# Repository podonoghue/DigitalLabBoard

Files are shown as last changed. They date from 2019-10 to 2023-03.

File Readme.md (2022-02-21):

# DigitalLabBoard
Digital Board for Undergraduate Laboratory  
Includes CPLD Programmer for XC2C64A

Folders:
* __Code_Design__ Software applications and firmware for on board microcontroller 
* __CommandLine__ Command line files using Xilinx S/W to prepare test images 
* __Documents__ Various resources associated with the project 
* __PCB_Design__ Altium Designer files for PCB 
* __Release_Files__ Release files for installation
* __VHDL_TestHardware__ Simple test projects for the CPLD 
 
[Lab manual](https://raw.githubusercontent.com/podonoghue/DigitalLabBoard/master/Laboratory%20Manual.pdf)
 
[Digital lab board documentation](https://raw.githubusercontent.com/podonoghue/DigitalLabBoard/master/PCB_Design/DigitalLabBoard/DigitalLabBoard_V4.PDF)  

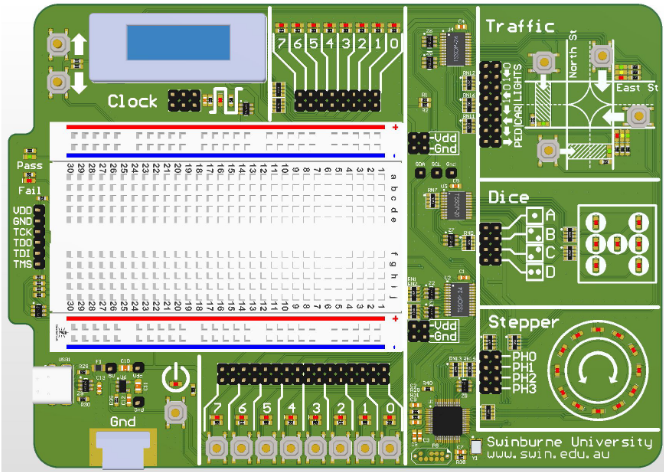
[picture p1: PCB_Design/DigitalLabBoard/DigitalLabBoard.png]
An image Board Image


[CPLD programmer documentation](https://raw.githubusercontent.com/podonoghue/DigitalLabBoard/master/PCB_Design/CPLD_Programmer/CPLD_Programmer_V2.PDF)  Note that a version of the programmer is built into the above lab board.

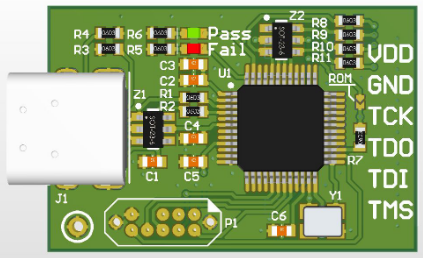
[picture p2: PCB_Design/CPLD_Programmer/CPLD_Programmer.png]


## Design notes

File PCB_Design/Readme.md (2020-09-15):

# PCB Designs

Folders:
* __CPLD_Programmer__ PCB design for standalone programmer
* __DigitalLabBoard__ PCB design for digitallab board

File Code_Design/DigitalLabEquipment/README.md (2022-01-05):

# Code for DigitalLabBoard
This code provides the following functions for the board:  
- Button debouncing and output for Button module.  
- Button debouncing, input monitoring and outputs for Traffic module.  
- Input monitoring and output LED control for the stepper module.  
- Control of the on-board clock generator.  
- SVD JTAG programmer.

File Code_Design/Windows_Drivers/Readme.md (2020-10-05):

# DigitalLabBoard - Driver
Windows Driver for Digital Lab Board and standalone CPLD programmer

Due to the need to create and sign windows driver .CAT files this sofwtare cannot be built on Linux.

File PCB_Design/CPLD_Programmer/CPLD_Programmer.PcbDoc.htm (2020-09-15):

Reporting Options

# File in Previous Format

Date | : | 15/09/2020
Time | : | 4:25:42 PM
Filename | : | \\vmware-host\Shared Folders\Documents\Development\DigitalLabBoard\PCB_Design\CPLD_Programmer\CPLD_Programmer.PcbDoc

Version | Warning

This file was generated by an earlier version of the software

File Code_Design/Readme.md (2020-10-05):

# DigitalLabBoard - Software
Software for Digital Lab Board and standalone CPLD programmer

Projects:
* __Bootloader_DigitalLogicBoard__ Software for boot-loader
* __Convert_XSVF_C__ Converts XSVF files to C array for embedding
* __CPLD_ProgrammerApp__ Windows application for CPLD programmer
* __DigitalLabEquipment__ Software for board
* __Documentation__ Links to Readme files
* __GenerateTables__ Creates tables describing JTAG state-machine and permitted transitions.
* __KinetisBootloaderApp__ WIN32 boot-loader application
* __Linux_Installer__ Linux installer (DEB file)
* __PackageFiles__ Where files are collected
* __PARSE_JEDEC__ 
* __Parse_XSVF_To_C__  
* __Shared__ Some files that get bundled when installer is built
* __Windows_Drivers__ WINUSB drivers for Windows (none needed for Linux)
* __Windows_Installer__ Windows installer (MSI file)
* __compareFiles__ 
* __xsvf_player__ Software for CPLD programmer
* __xsvf_rom_player__ Software for stand-alone CPLD programmer i.e. embedded CPLD XSVF array

This is an  __Eclipse__  workspace.  
Some projects required the __USBDM plugin__.

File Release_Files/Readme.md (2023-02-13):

# DigitalLabBoard
Release files for Digital Board for Undergraduate Laboratory  

* __Digital_Lab_Board_Drivers_1_1_0_Win_x64__ Signed drivers for Windows
* __DigitalLabEquipment_2023_02_14.elf__      Flash image for use with custom Kinetis bootloader
* __eee20001-lab-software_2.2.0.0-1-x86_64.deb__ CPLD programming software for Linux
* __EEE20001-Lab-Software-2020-01.msi__          CPLD programming software for Windows (original release)
* __EEE20001-Lab-Software-2023-02.msi__          CPLD programming software for Windows (latest)

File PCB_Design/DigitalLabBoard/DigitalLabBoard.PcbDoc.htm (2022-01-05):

Reporting Options

# File in Previous Format

Date | : | 22-Oct-21
Time | : | 3:15:27 PM
Filename | : | Z:\Documents\Development\DigitalLabBoard\PCB_Design\DigitalLabBoard\DigitalLabBoard.PcbDoc

Version | Warning
6.3 | CAUTION - Via connections to both hatched and solid signal layer polygons are now controlled by the polygon connect style rule. Re-pouring polygons may result in physical copper differences.
Summer 09 | CAUTION - File contains old violation objects. These violations are no longer supported & will not be loaded. Please run DRC after opening this file in order to refresh the violations.
Summer 09 | CAUTION - Existing testpoint rules and settings are used as fabrication testpoint information.
Release 12 | CAUTION - Air Gap Width previously controlled by Clearance rule is now controlled by Polygon Connect Style rule's newly introduced Air Gap Width (set to default value). Suggest reviewing each Polygon Connect Style rule's Air Gap Width attribute for correctness.
Release 13 | CAUTION - Silkscreen Over Component Pads Rules are converted to Silk To Solder Mask Clearance Rules. Suggest examining rule scopes for accuracy.

This file was generated by an earlier version of the software

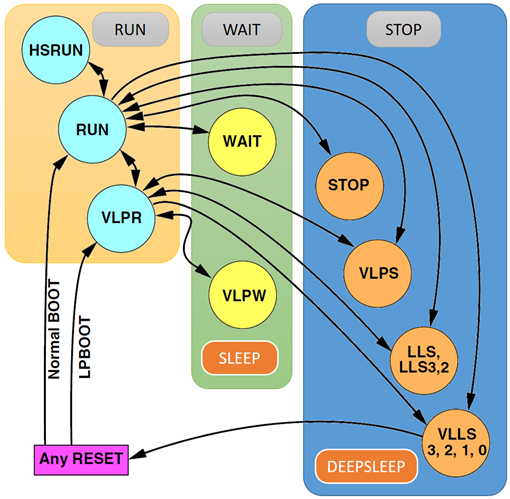
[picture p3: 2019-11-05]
Code_Design/KinetisBootloader/Project_Headers/KinetisPowerModes.png

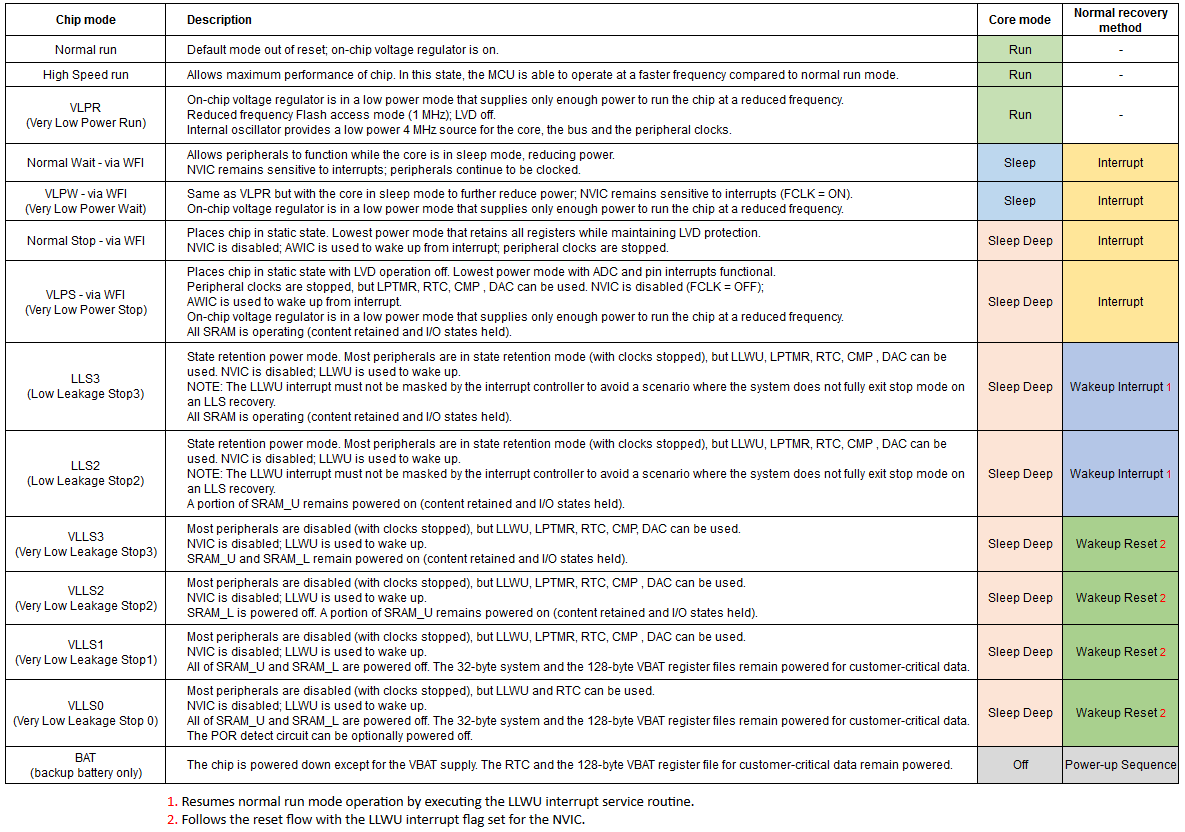
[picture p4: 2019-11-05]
Code_Design/KinetisBootloader/Project_Headers/PowerModes.png

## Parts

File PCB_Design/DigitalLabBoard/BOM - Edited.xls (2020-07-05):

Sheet: BOM Report
Bill of Materials |  |  | Bill of Materials for Project [DigitalLabBoard.PrjPCB] (No PCB Document Selected)
Source Data From: |  | DigitalLabBoard.PrjPCB
Project: |  | DigitalLabBoard.PrjPCB
Variant: |  | None
Logic Board |  |  |  |  |  |  | Unit cost |  | Per Board cost
Footprint | Comment | Farnell PN | Digikey | Designator | Description | Quantity | Small Qty | Large Qty | Small Qty | Large Qty
 |  |  |  |  | LCSC PCBA | 1 | $22.00 | $9.00 | $22.00 | $9.00
TSQFP50P900X900-48M | MK20DX128VLF5 | 2133571 (86 only) | MK20DX128VLF50-ND | U1 | 50MHz Cortex-M4 MCU | 1 | $8.86 | $7.01 | $8.86 | $7.01
USB4085-GF-A | USB4085-GF-A | 2924867 | 2073-USB4085-GF-ACT-ND | J8 | USB - C USB 2.0 Receptacle | 1 | $2.05 | $1.60 | $2.05 | $1.60 |  |  |  |  | $625.00
HDR1X6 straight | Header 1X6 | 1835481 | 609-3272-ND | P9 | Amphenol ICC 68000-106HLF | 1 | $0.55 | $0.98 | $0.55 | $0.98
HDR2X2S | Header 2x2 | 1622403 | 609-5699-ND/ A26534-02-ND | P10, P11 | Amphenol 77313-118-04LF/ TE Connectivity 4-102977-0-02 (longer pins) | 2 | $0.82 | $0.54 | $1.64 | $1.08 |  |  |  |  | $360.00
HDR2X3S | Header 2x3 | 2886106 | 609-5700-ND | P7 | Amphenol 77313-118-06LF | 1 | $0.58 | $0.38 | $0.58 | $0.38 |  |  | 100 | $58.37 | $5837.00
HDR2X4S | Header 2x4 |  | 609-5701-ND | P5, P6 | Amphenol 77313-118-08LF | 2 | $0.81 | $0.58 | $1.62 | $1.16 |  |  |  |  | $6822.00
HDR2X8S | Header 2x8 |  | 609-5704-ND | P1, P2, P3, P4 | Amphenol 77313-118-16LF | 4 | $1.11 | $0.83 | $4.44 | $3.32
Bumper_RBS-2 | Plastic Bumper | 1800864 1800862 | backup - RPC4821-ND | M1, M2, M3, M4, M5, M6, M7 | Plastic bumper/foot | 7 | $0.09 | $0.08 | $0.66 | $0.55 |  | Other | 100 | 32 | $3200.00
 |  |  |  |  |  |  |  | Parts | $20.40 | $16.08
 |  |  |  |  |  |  |  | 125 | $14.34 |  |  |  |  |  | $10022.00
 |  |  |  |  |  |  |  | 250 | $13.68
Breadboard - 300 holes | Breadboard - 300 Hole |  |  | B1 | Breadboard - 300 holes | 1 | $5.00 | $5.00 | $5.00 | $5.00 |  |  |  |  |  | Digikey online Quote
OLED_Display_128x32 | OLED_Display |  |  | OLED | OLED Display 128x32 pixels, I2C interface | 1 | $2.00 | $2.00 | $2.00 | $2.00 |  |  | Units | Cost | Total | 125 | 250
USB Type-A to USB-C R/A | USB Lead |  |  |  | USB Type-A to USB-C R/A lead | 1 | $6.00 | $6.00 | $6.00 | $6.00 | Base Board | Assembly | 250 | $9.00 | $2250.00
Decor 002560 | 900ml Plastic Box |  |  |  | Tellfresh Storer, Oblong 900ml, 203x143x53 | 1 | $3.33 | $3.33 | $3.33 | $3.33 |  | Parts | 125 | $14.34 | $1792.50 | $1792.5 | $3420
Patch Leads | 6" leads |  |  |  | M-M individual 6" leads - set of 10 | 1 | $3.38 | $2.50 | $3.38 | $2.50 |  | Other | 125 | $24.10 | $3012.92
Patch Leads | 6" leads |  |  |  | M-F individual 6" leads - set of 15 | 1 | $5.05 | $3.75 | $5.05 | $3.75 |  |  |  |  | $7055.42
Programming Lead | 3" lead |  |  |  | 6-way F-F 3" lead - 1 only | 1 | $2.06 | $1.52 | $2.06 | $1.52
 |  | Digikey cart | https://www.digikey.com.au/BOM/View?id=8130251 |  |  |  | $10.48 | Other | $26.82 | $24.10 | CPLD | Assembly | 250 | $1.22 | $305.00
CPLD Breakout |  |  |  |  |  |  |  |  |  |  |  | Parts | 125 | $8.35 | $1043.75 | $1043.75 | $1980
Footprint | Comment | Farnell PN | Digikey | Designator | Description | Quantity |  |  |  |  |  |  |  |  | $1348.75
CPLD Breakout | LCSC PCBA |  |  |  | LCSC PCBA | 1 |  | $1.22 | $0.00 | $1.22
 |  |  |  |  |  |  |  |  |  |  | Power | Assembly | 250 | $1.22 | $305.00
XC2C64A-7VQG44C | Xilinx CPLD | 2831286 | Backup 122-1410-ND |  |  | 1 | $5.28 | $5.27 | $5.28 | $5.27 |  | Parts | 125 | $2.29 | $286.25 | $286.25 | $520
HDR1x20 straight | Header 1x20 | 2892385 | 609-3253-ND |  | Amphenol ICC 68000-120HLF | 2 | $1.53 | $1.16 | $3.06 | $2.32 |  |  |  |  | $591.25
HDR1X6 straight | Header 1X6 | 1835481 | 609-3272-ND |  | Amphenol ICC 68000-106HLF | 1 | $0.55 | $0.98 | $0.55 | $0.98
 |  | Digikey cart | https://www.digikey.com.au/BOM/View?id=8130245 |  |  |  |  | Parts | $8.89 | $8.57 |  |  |  |  | $8995.42
 |  |  |  |  |  |  |  | 125 | $8.35
 |  |  |  |  |  |  |  | 250 | $7.92
 |  |  |  |  |  |  |  |  |  |  | Phase 2 | $7000.00 | extra 125
Breadboard Power
Footprint | Comment | Farnell PN | Digikey | Designator | Description | Quantity |  |  |  |  | 125 | $90.00 | $11250.00
Breadboard-power | LCSC PCBA |  |  |  | LCSC PCBA | 1 |  | $1.22 | $0.00 | $1.22 | 125 | $25.00 | $3125.00
 |  |  |  |  |  |  |  |  |  |  |  |  | $14375.00
HDR2X2S | Header 2x2 | 1622403 | 609-5699-ND | P1, P2 | Amphenol 77313-118-04LF | 2 | $0.40 | $0.26 | $0.80 | $0.52
HDR1X2S | Header, 2-Pin | 2751379 | 609-3500-ND | P3, P4 | Amphenol 68000-102HLF | 2 | $0.30 | $0.20 | $0.60 | $0.40
BCS-102-L-D-TE | Header 2x2, Female | 2984530 | SAM1008-02-ND | P5, P6 | Samtec BCS-102-L-D-TE | 2 | $1.05 | $0.75 | $2.10 | $1.50
 |  | Digikey cart | https://www.digikey.com.au/BOM/View?id=8130238 |  |  |  |  | Parts | $3.50 | $2.42 | 50 | 200
 |  |  |  |  |  |  |  | 125 | $2.29
 |  |  |  | Sparkfun PRT-10366 | Jumper Wire - 0.1", 6-pin, 4" |  |  | 250 | $2.08
 |  |  |  | Robot Gear SKU-002545 | Jumper Wire - 0.1", 6-pin, 4"
 |  |  |  | Pololu DIY | https://www.pololu.com/category/71/wires-with-pre-crimped-terminals
 |  |  |  |  |  |  |  |  |  |  | 635.67 | 2356.19

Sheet: Leads
 |  |  | /set | /set
 |  |  |  |  |  |  |  | 125
https://www.pololu.com/product/3330 | Wires with Pre-Crimped Terminals 10-Pack F-F 3" Black | $2.12 | 0.1 | $0.21 | 1 | 1 + 1 + 1 + 2 Makes 10 sets of programming cables | $2.12 | 12.5 | $26.50
https://www.pololu.com/product/3332 | Wires with Pre-Crimped Terminals 10-Pack F-F 3" Red | $2.12 | 0.1 | $0.21 | 1 |  | $2.12 | 12.5 | $26.50
https://www.pololu.com/product/1806 | Wires with Pre-Crimped Terminals 50-Piece 10-Color Assortment F-F 3" | $7.99 | 0.1 | $0.80 | 1 |  | $7.99 | 12.5 | $99.88
https://www.pololu.com/product/1905 | 0.1" (2.54mm) Crimp Connector Housing: 1x6-Pin 10-Pack | $0.71 | 0.2 | $0.14 | 2 |  | $1.42 | 25 | $17.75
 |  |  |  | $1.36
https://www.pololu.com/product/1702 | Premium Jumper Wire 50-Piece 10-Color Assortment M-M 6" | $11.24 | 0.2 | $2.25 | 2 | 2 + 3 Makes 10 sets of jump leads | $22.48 | 25 | $281.00
https://www.pololu.com/product/1701 | Premium Jumper Wire 50-Piece 10-Color Assortment M-F 6" | $11.24 | 0.3 | $3.37 | 3 |  | $33.72 | 37.5 | $421.50
 |  |  |  | $6.99 |  |  | $6.98 |  | $873.12
 |  | M-M | M-F | CPL M-M | PWR M-M
E1 | P1 | 2 | 6 |  | 2
 | P2 | 2 | 4
 | P3 |  | 5 | 2
 | P4 | 8 | 3 | 2
E2 | P1-3 |  | 8 | 2
 | P4 | 2 | 2
E3 | P1 |  | 6 | 2
 | P2a |  | 5 | 2
 | P2b |  | 5 | 2
 | P2c |  | 6 | 2
 | P3 | 5 | 3 |  | 2
 | P4 |  | 6 | 2
E4 | P1 |  | 9 | 2
 | P2 |  | 5 | 2
 | P3 |  | 6 | 2
Project | Stepper |  | 8 | 2
 | Traffic |  | 11 | 2
 |  | 8 | 11 | 2
 |  | 10 | 15

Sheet: LCSC BOM
Footprint | Comment | Farnell PN | Digikey | LCSC | Designator | Description | Quantity
TSSOP24_N | PCA9555PW,118 | 2101299 | 568-1058-1-ND | C128392 | U2 | 16-bit I2C I/O Expander (TSSOP24) PUPs on I/O pins | 1
Crystal_SMD_3.2x2.5 | 16 MHz |  |  | C13738 | Y1 | Crystal SMD 3.2 x 2.5 x 0.7 mm | 1
CCNP1608-0603 | 100nF |  |  | C14663 | C1, C2, C3, C4, C5, C6, C7, C13, C14 | Capacitor non-polar SMT 0603 | 9
CCNP1608-0603 | 1uF |  |  | C15849 | C9 | Capacitor | 1
CCNP2012-0805 | 10uF |  |  | C15850 | C10, C11 | Capacitor | 2
CR1206-0603_X4_L | 1K |  |  | C20197 | RN8, RN10, RN19 | SMT x4 Resistor Array | 3
CR1608-0603 | 1K |  |  | C21190 | R3, R4, R5, R6, R7, R8, R9, R10, R11, R12, R13, R14, R15, R16, R17, R18, R19, R20, R22, R23, R24, R26, R27, R32, R39, R41 | Resistor SMT 0603 | 26
CR1608-0603 | 100R |  |  | C22775 | R36, R42, R43, R44, R45 | Resistor SMT 0603 | 5
LED1608-0603-RED | LED Red | 1581239 |  | C2286 | D1, D2, D3, D4, D5, D6, D7, D8, D17, D_CLOCK, D_Fail, D_REW, D_RNS, DIE_LED_A, DIE_LED_B1, DIE_LED_B2, DIE_LED_C1, DIE_LED_C2, DIE_LED_D1, DIE_LED_D2, LED_0, LED_1, LED_2, LED_3, LED_4, LED_5, LED_6, LED_7, Step_LED1, Step_LED2, Step_LED3, Step_LED4, Step_LED5, Step_LED6, Step_LED7, Step_LED8, Step_LED9, Step_LED10, Step_LED11, Step_LED12 | LED 0603 Red | 40
CR1608-0603 | 33R |  |  | C23140 | R28, R31 | Resistor SMT 0603 | 2
CR1608-0603 | 4.7K |  |  | C23162 | R1, R2 | Resistor SMT 0603 | 2
CR1608-0603 | 470R |  |  | C23179 | R40 | Resistor SMT 0603 | 1
CR1608-0603 | 5.1K |  |  | C23186 | R29, R30 | Resistor SMT 0603 | 2
CR1608-0603 | 560R |  |  | C23204 | R21, R25 | Resistor SMT 0603 | 2
CCNP1608-0603 | 2.2uF |  |  | C23630 | C8 | Capacitor | 1
CR1206-0603_X4_L | 470R |  |  | C25510 | RN1, RN2, RN5, RN6, RN9, RN11, RN12, RN14, RN15 | SMT x4 Resistor Array | 9
TSSOP24_N | PCA9535PW,118 | 2776149 | 568-10296-1-ND | C255606 | U4 | 16-bit I2C I/O Expander (TSSOP24) NO PUPs on I/O pins | 1
CR1608-0603 | 10K |  |  | C25804 | R33, R34, R35, R37, R38 | Resistor SMT 0603 | 5
CR1206-0603_X4_L | 10K |  |  | C29718 | RN3, RN4, RN7, RN13, RN16, RN17 | SMT x4 Resistor Array | 1
SMD-SW-4_5.1x5.1x3.5_M | SMD-SW-4_5.1x5.1x3.5_M |  |  | C318886 | S_FREQ_DOWN, S_FREQ_UP | Tactile Switch SPST 5.10mm X 5.10mm (1.5mm=C318884) (2.0mm=C318888) (3.5mm=C318886) | 2
SMD-SW-4_5.1x5.1x2.0_M | SMD-SW-4_5.1x5.1x2.0_M |  |  | C318888 | POWER_BTN, S1, S2, S3, S4, S5, S6, S7, S8, S_CEW, S_CNW, S_PEW, S_PNS | Tactile Switch SPST 5.10mm X 5.10mm (1.5mm=C318884) (2.0mm=C318888) (3.5mm=C318886) | 13
SOT457_N | CM1293A-04SO | 2533258 | CM1293A-04SOOSCT-ND | C393377 | Z1, Z2, Z3, Z4, Z5, Z6, Z7, Z8, Z9, Z10, Z11 | Ultra low capacitance quadruple rail-to-rail ESD protection | 11
TSSOP20_N | 74HC541PW,118 | 2444902 | 1727-5960-1-ND | C5657 | U3, U5 | Octal 3-State Buffer/Line Driver/LineReceiver | 2
CCNP1608-0603 | 10nF |  |  | C57112 | C12 | Capacitor | 1
SMD0805-050 | SMD0805-050 |  |  | C66452 | F1 | PTC Resetable Fuse 0805 0.5A hold | 1
LED1608-0603-Yellow | LED Yellow | 5790852 |  | C72038 | D_AEW, D_ANS | LED 0603 Yellow | 2
LED1608-0603-GREEN | LED Green | 1581242 |  | C72043 | D_GEW, D_GNS, D_Pass, D_PEW, D_PNS | LED 0603 Green | 5 | Unit cost |  | Per Board cost
SOT-23-5_L | SPX3819M5-L-3-3/TR | 2889625 | 1016-1873-1-ND | C9055 | U6 | 3.3V LDO with enable | 1 | 5 of cost | >100 cost | 5 of | >250 cost
 |  |  |  |  |  | LCSC PCBA | 1 | $22.00 | $9.00 | $22.00 | $9.00
 |  |  |  |  |  |  |  |  |  |  |  |  |  |  | $625.00
 |  |  |  |  |  |  | 1 | Unit cost |  | Per Board cost |  |  |  |  | $360.00
 |  |  |  |  |  |  |  | 5 of cost | >100 cost | 5 of | >250 cost |  | 100 | $58.37 | $5837.00
TSQFP50P900X900-48M | MK20DX128VLF5 | 2133571 (86 only) | MK20DX128VLF50-ND |  | U1 | 50MHz Cortex-M4 MCU | 1 | $8.86 | $7.01 | $8.86 | $7.01 |  |  |  | $6822.00
USB4085-GF-A | USB4085-GF-A | 2924867 | 2073-USB4085-GF-ACT-ND |  | J8 | USB - C USB 2.0 Receptacle | 1 | $2.05 | $1.60 | $2.05 | $1.60
HDR2X2S | Header 2x2 | 1622403 | 609-5699-ND |  | P1, P5 | Amphenol 77313-118-04LF | 2 | $0.40 | $0.26 | $0.80 | $0.52 | Other | 100 | 32 | $3200.00
HDR2X3S | Header 2x3 | 2886106 | 609-5700-ND |  | P7 | Amphenol 77313-118-06LF | 1 | $0.58 | $0.38 | $0.58 | $0.38
HDR2X4S | Header 2x4 |  | 609-5701-ND |  | P5, P6 | Amphenol 77313-118-08LF | 2 | $0.81 | $0.58 | $1.62 | $1.16 |  |  |  | $10022.00
HDR2X8S | Header 2x8 |  | 609-5704-ND |  | P1, P2, P3, P4 | Amphenol 77313-118-16LF | 4 | $1.11 | $0.83 | $4.44 | $3.32
Bumper_RBS-2 | Plastic Bumper | 1800864 1800862 | backup - RPC4821-ND |  | M1, M2, M3, M4, M5, M6 | Plastic bumper/foot | 6 | $0.09 | $0.08 | $0.56 | $0.47

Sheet: Spent
 |  |  |  |  |  | 1 | megabuy | $217.48 | 30 * USB-C leads |  | 30 | $217.48 | $7.25
 | Digikey | Initial Protoytpes | $189.27 | Estimate |  | 2 | mwave | $305.85 | 30 * USB-C leads |  | 30 | $305.85 | $10.20
 | Digikey | Initial Protoytpes | $151.99 | Estimate |  | 3 | JLCPCB | $238.25 | pcb proto
 |  |  |  |  |  | 4 | ebay | $260.70 | 30 * USB-C leads |  | 30 | $260.70 | $8.69
2019-11-29 | JLCPCB | LabBoard_V1 + Misc boards (MK_Programmer, adapters etc) | $209.15 |  | $218.62 | 5 | core electronics | $67.72 | headers to try???
2019-12-11 | JLCPCB | LabBoard_V2 + CPLD_Programmer_V1 + Misc boards (adapters etc) | $158.76 |  | $165.96 | 6 | core electronics | $7.50
2020-01-30 | JLCPCB | LabBoard_V3 + CPLD Tester + Jigs (LabBoard_V3 + CPLD) | $245.83 |  | $256.97 | 7 | element14 | $307.24 | $180 consumables | $180.00
2020-01-30 | JLCPCB | PCB 1st run - 30*CPLD, 30*LabBoard_V4, 5*CPLD_Programmer_V2 | $399.93 |  | $418.05 | 8 | ebuy | $72.20 | 20 * Breadboards |  |  |  |  | 20 | $72.20 | $3.61
2020-01-30 | Digikey | Parts for above (30*CPLD, 125*LabBoard) | $2300.00 |  |  | 9 | aliexpress | $290.00 | Oleds
 |  | OLEDs - 125*4 | $500.00 | Estimate |  | 10 | PAYPAL *EBUY7 |  | Oscilloscope Clips - last year | $75.73
 |  | Protoboards - 125 * 5 | $625.00 | Estimate |  | 11 | JLCPCB.COM | $412.91 | Prototype
 |  | USB Leads - 125 * 9 | $1125.00 | Estimate |  | 12 | DKC DIGI-KEY CORP | $2264.95 | Parts
2020-02-03 | JLCPCB | 120*Power + 15*TDR_Pulser * Jigs (LabBoard_V3 + CPLD) | $84.88 |  | $88.44 | 13 | skycomp | $273.10 | 25 * USB-C leads |  | 25 | $273.10 | $10.92
2020-02-07 |  | Pololu - leads 125*(M-M, M-F, Programming cable) | $1500.00 | Approx |  | 14 | pololu | $1448.71 | Leads
2020-03-02 |  | Element-14, More parts for base + 25 x CPLD | $640.00 | Approx |  | 15 | banggood | $134.35 | 20 * Breadboards |  |  |  |  | 20 | $134.35 | $6.72
2020-03-02 |  | PCB 2nd Run - 90 *CPLD | $224.40 | Approx | $224.40 | 16 | element14 | $654.81 | Parts
 |  |  |  |  |  | 17 | Fedex | $152.22 | Pololu Import duty
 |  |  |  |  |  | 18 | JLCPCB | $85.39 | Prototype
 |  |  |  |  |  | 19 | UPS | $99.69 | DigiKey import duty??
 | JLCPCB | 120*LabBoard_V4 | $1200.00 | Estimate |  | 20 | JLP |  | No idea what JLP is | $399.98
 |  |  |  |  |  | 21 | Aiexpress | $301.20 | 100 x OLED |  |  |  |  |  |  |  | 100 | $301.20 | $3.01
 |  |  |  |  |  | 22 | Freetronics |  | IOT for P Branch | $908.50
 |  |  | $9554.21 |  |  | 23 | BengGoods |  | Workshop Store, Arduino etc | $81.91
 |  |  |  |  |  | 24 | JLCPCB |  | Repeated charge | $157.33
 |  |  |  |  |  | 25 | digikey | $189.27 | Prototype Parts
 |  |  |  |  |  | 26 | digikey | $151.99 | Prototype Parts
 |  |  |  |  |  | 27 | JLCPCB | $136.61 | Digital Lab 1st Proto
 |  |  |  |  |  | 28 | JLCPCB | $113.16 | CPLD Tester+CPLD Proto 1 (Iain)
 |  |  |  |  |  | 29 | megabuy | $47.10 | 5 * USB Cables |  | 5 | $47.10 | $9.42
 |  |  |  |  |  | 30 | ebay | $19.14 | 5 * USB Cables |  | 5 | $19.14 | $3.83
 |  |  |  |  |  | 31 | mwave | $35.19 | 5 * USB Cables |  | 5 | $35.19 | $7.04
 |  |  |  |  |  | 32 | altronics |  | Semester 1 Consumables | $345.82
 |  |  |  |  |  | 33 | rapidonline | $144.34 | gull-wing tips, thin pins
 |  |  |  |  |  | 34 | JLCPCB |  | Should be 5th year project budget | $208.38
 |  |  |  |  |  | 35 | aliexpress | $64.20 | 5 * OLED
 |  |  |  |  |  | 36 | littlebird | $101.90 | Jumper wires
 |  |  |  |  |  | 37 | gearbest | $224.73 | 40 x breadboards |  |  |  |  | 40 | $224.73 | $5.62
 |  |  |  |  |  | 38 | JLCPCB |  | Should be 5th year project budget | $157.33
 |  |  |  |  |  |  |  | $8821.90 |  | $2514.98 | 130 | 1158.56 | 8.912 | 80 | 431.28 | 5.391

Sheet: Request
90 | 90 | 8100
90 | 30 | 2700
 |  | 10800

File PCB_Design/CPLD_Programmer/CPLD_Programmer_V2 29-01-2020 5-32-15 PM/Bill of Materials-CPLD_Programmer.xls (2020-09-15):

Comment | Description | Designator | Footprint | LibRef | Quantity | Farnell PN | Digikey
100nF | Capacitor non-polar SMT 0603 | C1, C3, C4, C5, C6 | CCNP1608-0603_N | Cap_CCNP_0603 | 5
2.2uF | Capacitor non-polar SMT 0603 | C2 | CCNP1608-0603_N | Cap_CCNP_0603 | 1
LED Red | LED 0603 Red | D1 | LED1608-0603-RED_N | LED-0603-Red | 1 | 1581239
LED Green | LED 0603 Green | D2 | LED1608-0603-GREEN_N | LED-0603-Green | 1 | 1581242
USB4085-GF-A | USB-C, USB 2.0 Receptacle Connector 16 Position Through Hole, Right Angle | J1 | USB4085-GF-A |  | 1 | 2924867 | 2073-USB4085-GF-ACT-ND
Header, 6-Pin | Header, 6-Pin | J2 | SAMTEC-SMH-106-02-X-S | Header Female 1x6H-SMT | 1 | 2084265 (sim) | SAM15786-ND
330R | Resistor SMT 0603 | R1, R2 | CR1608-0603_N | Res_CR0603 | 2
5.1K | Resistor SMT 0603 | R3, R4 | CR1608-0603_N | Res_CR0603 | 2
1K | Resistor SMT 0603 | R5, R6 | CR1608-0603_N | Res_CR0603 | 2
10K | Resistor SMT 0603 | R7 | CR1608-0603_N | Res_CR0603 | 1
100R | Resistor SMT 0603 | R8, R9, R10, R11 | CR1608-0603 | Res_CR0603 | 4
LinkOpen |  | ROM | SolderBridge(Open) | LinkOpen | 1
TP | Test Point | TP1 | TP | TP | 1
MK20DX128VLF5 | Arm Cortex M4 | U1 | TSQFP50P900X900-48M | MK20DX128VLF5 | 1
16 MHz | Crystal SMD 3.2 x 2.5 x 0.7 mm | Y1 | Crystal_SMD_3.2x2.5 | Crystal 16MHz | 1
CM1293A-04SO | Ultra low capacitance quadruple rail-to-rail ESD protection | Z1, Z2 | SOT457_N | CM1293A-04SO | 2 | 2533258 | CM1293A-04SOOSCT-ND

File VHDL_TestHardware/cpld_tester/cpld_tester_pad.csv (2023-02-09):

Release 8.1i - Fit P.20131013
Copyright(c) 1995-2003 Xilinx Inc. All rights reserved
2- 4-2023 6:11PM
NOTE: This file is designed to be imported into a spreadsheet program
such as Microsoft Excel for viewing | printing and sorting. The comma ' | '
character is used as the data field separator.
This file is also designed to support parsing.
Input file: cpld_tester.ngd
output file: cpld_tester_pad.csv
Part type: xc2c64a
Speed grade: -5
Package: vq44
Pinout by Pin Number:
----- | ----- | ----- | ----- | ----- | ----- | ----- | ----- | ----- | -----
Pin Number | Signal Name | Pin Usage | Pin Name | Direction | IO Standard | IO Bank Number | {blank} | Slew Rate | Termination | {blank} | Voltage | Constraint
P1 | clock | GCK | I/O/GCK2 |  | LVCMOS33 | 1 |  | FAST
P2 | leds<18> | O | I/O | OUTPUT | LVCMOS33 | 1 |  | FAST
P3 | leds<17> | O | I/O | OUTPUT | LVCMOS33 | 1 |  | FAST
P4 | GND |  | GND
P5 | leds<16> | O | I/O | OUTPUT | LVCMOS33 | 1 |  | FAST
P6 | leds<15> | O | I/O | OUTPUT | LVCMOS33 | 1 |  | FAST
P7 |  | VCCIO-3.3 | VCCIO |  |  | 1
P8 | leds<14> | O | I/O | OUTPUT | LVCMOS33 | 1 |  | FAST
P9 | TDI |  | TDI
P10 | TMS |  | TMS
P11 | TCK |  | TCK
P12 | leds<0> | O | I/O | OUTPUT | LVCMOS33 | 1 |  | FAST
P13 | leds<1> | O | I/O | OUTPUT | LVCMOS33 | 1 |  | FAST
P14 | leds<2> | O | I/O | OUTPUT | LVCMOS33 | 1 |  | FAST
P15 |  | VCC | VCC
P16 | leds<3> | O | I/O | OUTPUT | LVCMOS33 | 1 |  | FAST
P17 | GND |  | GND
P18 | leds<4> | O | I/O | OUTPUT | LVCMOS33 | 2 |  | FAST
P19 | leds<5> | O | I/O | OUTPUT | LVCMOS33 | 2 |  | FAST
P20 | leds<6> | O | I/O | OUTPUT | LVCMOS33 | 2 |  | FAST
P21 | leds<7> | O | I/O | OUTPUT | LVCMOS33 | 2 |  | FAST
P22 | leds<8> | O | I/O | OUTPUT | LVCMOS33 | 2 |  | FAST
P23 | leds<9> | O | I/O | OUTPUT | LVCMOS33 | 2 |  | FAST
P24 | TDO |  | TDO
P25 | GND |  | GND
P26 |  | VCCIO-3.3 | VCCIO |  |  | 2
P27 | leds<10> | O | I/O | OUTPUT | LVCMOS33 | 2 |  | FAST
P28 | leds<11> | O | I/O | OUTPUT | LVCMOS33 | 2 |  | FAST
P29 | leds<12> | O | I/O | OUTPUT | LVCMOS33 | 2 |  | FAST
P30 | leds<13> | O | I/O/GSR | OUTPUT | LVCMOS33 | 2 |  | FAST
P31 | leds<31> | O | I/O/GTS2 | OUTPUT | LVCMOS33 | 2 |  | FAST
P32 | leds<30> | O | I/O/GTS3 | OUTPUT | LVCMOS33 | 2 |  | FAST
P33 | leds<29> | O | I/O/GTS0 | OUTPUT | LVCMOS33 | 2 |  | FAST
P34 | leds<28> | O | I/O/GTS1 | OUTPUT | LVCMOS33 | 2 |  | FAST
P35 |  | VCCAUX | VAUX
P36 | leds<27> | O | I/O | OUTPUT | LVCMOS33 | 2 |  | FAST
P37 | leds<26> | O | I/O | OUTPUT | LVCMOS33 | 2 |  | FAST
P38 | leds<25> | O | I/O | OUTPUT | LVCMOS33 | 2 |  | FAST
P39 | leds<24> | O | I/O | OUTPUT | LVCMOS33 | 1 |  | FAST
P40 | leds<23> | O | I/O | OUTPUT | LVCMOS33 | 1 |  | FAST
P41 | leds<22> | O | I/O | OUTPUT | LVCMOS33 | 1 |  | FAST
P42 | leds<21> | O | I/O | OUTPUT | LVCMOS33 | 1 |  | FAST
P43 | leds<20> | O | I/O/GCK0 | OUTPUT | LVCMOS33 | 1 |  | FAST
P44 | leds<19> | O | I/O/GCK1 | OUTPUT | LVCMOS33 | 1 |  | FAST
To preserve the pinout above for future design iterations in
Project Navigator simply execute the (Lock Pins) process
located under the (Implement Design) process in a toolbox named
(Optional Implementation Tools) or invoke PIN2UCF from the
command line. The location constraints will be written into your
specified UCF file

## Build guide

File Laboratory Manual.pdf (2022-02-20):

aculty of Science and Engineering Technology Higher Education Division

# Laboratory Manual EEE20001

## Digital Electronics Design

Version date 10 March 2020

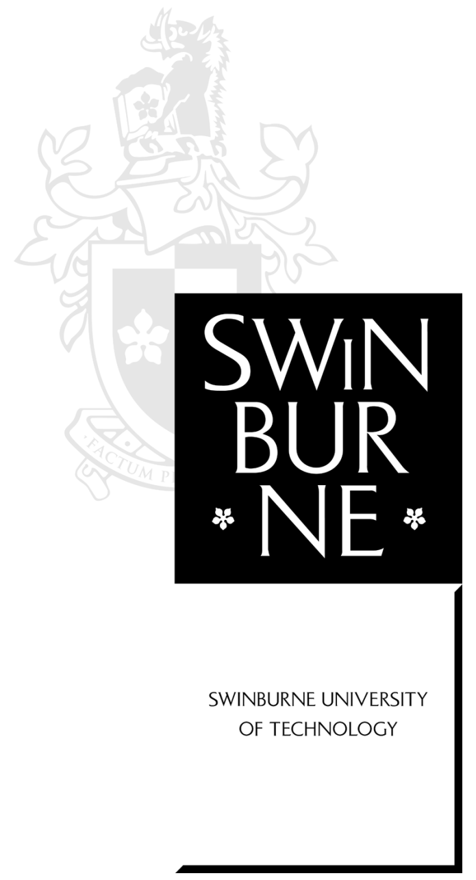
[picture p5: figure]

EEE20001 Digital Electronics Design | Lab Manual | 2 of 15

Laboratory Program
The laboratory program is intended to re-enforce the material covered in lectures and tutorials by a practical program involving design and implementation of digital circuits. This re-enforcement will be a natural outcome of individuals completing the design work, debugging the resulting design implementations and finally obtaining the desired operation. This process involves a fair amount of effort, but the reward is a much better understanding of the material and the gaining of some real-world abilities – especially fault finding and debugging!
I urge all students to put in the required effort rather than seeking the obvious short cuts.
- The laboratory program is completed by groups of 2 students with only a single submission required from the group. To support the program, each group is provided with their own set of laboratory hardware. This allows a great deal of the work to be completed out of formal laboratory time. Both group members will be required to sign for this equipment and return it in good order at the completion of the laboratory program. Results for the unit will be withheld until the equipment is returned.
- You will also need to use Electronic Design Automation (EDA) software. This software is only available for student use on campus in the AD207, AD208 laboratories and on limited machines in the library. These first two are general access laboratories and students are expected to access the labs out of scheduled class time. The required software may also be obtained for private use. Details are available from Canvas.
- The laboratory program consists of 4 single laboratory sessions and a project which extends over 3 laboratory sessions.
- The first 4 laboratory exercises require submission of a work sheet at the completion of the laboratory session. This sheet is to be submitted to the laboratory supervisor. The work sheet has required preliminary work that must be completed before entering the laboratory. Various stages of the work sheet require initialling by the laboratory supervisor to record correct completion and demonstration of work done. It is the student’s responsibility to ensure that the demonstration and recording of such occur during the laboratory session. The sheet should be handed in at the completion of the session or otherwise recorded by the laboratory supervisor. Failure to complete preliminary work before the laboratory session may result in the student(s) being excluded from the session and receiving no marks.
- The assessment of laboratory exercises will be based upon demonstration of work, understanding of operation and written submissions. Laboratory work will require an individual oral presentation of results.
- The VHDL project is completed over 3 laboratory sessions but again it is expected that much of the work will be completed outside of the formal sessions. These sessions should be viewed as an opportunity to ask questions and obtain help with specific problems. The project requires a single written report for each laboratory group. Note however, that individual assessment will still occur in the laboratory sessions. The practical demonstration is to occur during scheduled laboratory times. Submissions will not be accepted by email or electronic form.
- Late submissions for laboratory work without adequate reason and prior arrangement may attract zero marks. Adequate reason will usually be similar to an unanticipated medical problem extending for a significant time

Closed Footwear must be worn in the laboratory. Students wearing open-toed shoes or thongs will be asked to leave the laboratory and will be unable to complete the work.

## Rules for EEE20001 Laboratories

Section 1: Rules for dealing with equipment during laboratory sessions
- Never build or alter a circuit while power is applied to it.
- Do not connect power to a circuit until the circuit is finished and you have carefully checked your work.
- Keep your work area dry. Keep any food and drink bottles in your bag and well away from the work bench.
- Make sure you know where the safety equipment in the laboratory is located (such as the fire extinguisher, first-aid kit, emergency power cut-off button (where installed) and the nearest phone and list of safety personnel).
- Faulty equipment or equipment with suspect wiring or other safety concerns must be switched OFF at the power point immediately and reported to the demonstrator
- Equipment that does not have a current electrical tag must not be used-report this to the technical staff or supervisor
- On completion of experimental work all equipment is to be switched off, equipment and leads stored away appropriately, and bench areas left in a tidy and safe state.
Section 2: Conduct requirements during laboratory sessions
The University executes safety drills without warning. Be prepared to follow instructions from university staff and/or wardens to evacuate the building in a safe and orderly manner.
All students are expected to respect the rights and sensibilities of their fellow students and teaching staff. The University has rigorous anti-discrimination and harassment policies and procedures.
The following specific safety procedures must be followed in the laboratory:
- Open-toed shoes (including thongs, or sandals etc., or bare feet) are not permitted in the Electronics laboratory, and students may be excluded if they have inappropriate or inadequate footwear.
- Drink (including water from drinking bottles) or food is not permitted in the laboratory.
- Sitting on laboratory benches is prohibited.
- You should never run in the laboratory. Make sure bags and other articles do not obstruct the exits or constitute a tripping hazard. Place them as indicated by your supervisor or the technical staff.
Section 3: Relevant Safety Information for laboratory sessions
- First Aid
If you, or someone you are with, require first aid at any time while you are in the labs, please contact your laboratory demonstrator and/or the laboratory technician immediately or contact a First Aid officer as shown on the ‘First Aid’ poster near the telephone or near the entry. If you are unable to find a staff member, you must ring 9214 3333, the emergency number for Campus Security who are First Aid qualified. You might also need to ring the Campus Medical Centre on 9214 8483.
If you yourself are feeling unwell or dizzy when participating in an experiment, stop immediately, sit down and ask someone to notify the demonstrator or laboratory technician.
Any accident must be reported to the demonstrator or laboratory technician.

Laboratory Equipment
The following Equipment is provided:
- Digital Logic Board
- This incorporates: Switches, LEDs, Clock, Dice, Traffic Intersection and Stepper Motor modules.
- USB-C lead
- Bread-board wires
- CPLD module
- Power bridging PCB.
- Programming cable from baseboard to CPLD
- A selection of SSI and MSI integrated circuits and some discrete components. Use of this laboratory equipment is described in the following sections.
Prototyping Board
The prototyping board is attached to the baseboard but is electrically isolated from it. Connection to the power on the baseboard is made through a small PCB that bridges between the breadboard and baseboard as shown.
The breadboard has holes connected in vertical groups of 5 in the main part of the board and horizontal strips that extend for the width of the board at top and bottom. These provide convenient power supply locations and are indicated in red for Vdd and blue for Gnd. This allows access to the power rails from either side of the IC packages. It is also desirable to place two 100nF multi-layer ceramic (MLC) capacitors across the power supply rails to reduce noise. The ICs are placed so that they straddle the channel in the middle of the board. When placing ICs in the board they should be spaced apart to allow easier removal by levering them up at both ends. Do not try removing them by hand as it will bend the pins and even cause injury. Yes - I have seen students with neat rows of holes in their fingers from the sharp pins

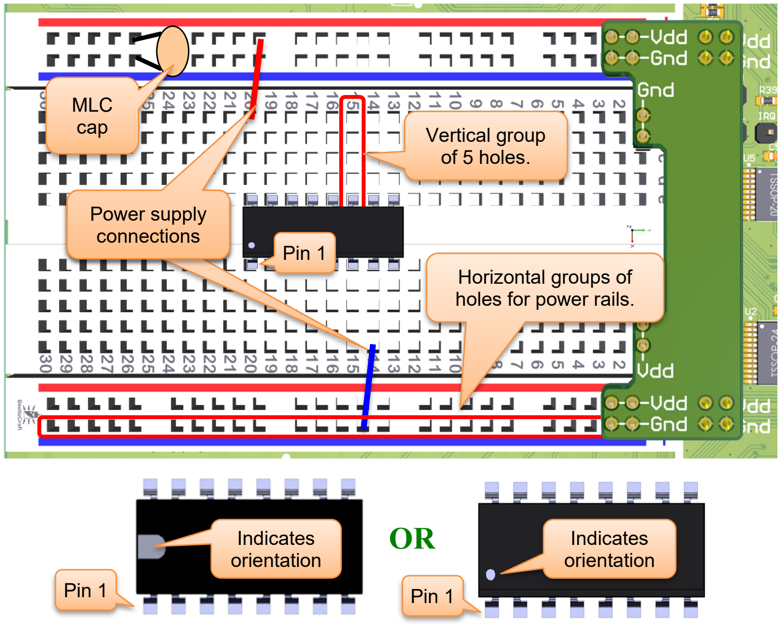
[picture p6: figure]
Vertical group of 5 holes.; MLC cap; Power supply connections; Indicates orientation; Pin 1; Horizontal groups of holes for power rails.

The CPLD should be placed so that its power supply connections match the inner connections on the small bridging PCB.
Do not try removing the CPLD by hand as it may bend the pins.
To remove the CPLD first remove the bridging board and the programming cable, and then lever the module up at BOTH ends in turn until it is released from the breadboard.

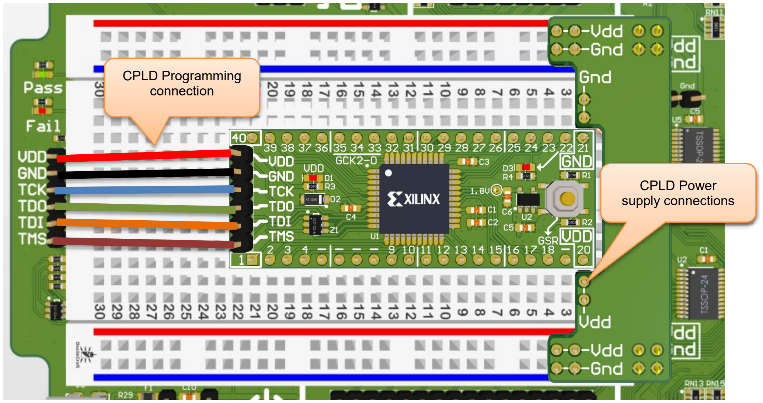
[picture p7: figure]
Power supply connections; CPLD Power supply connections; CPLD Programming connection

Important Warnings
✓ Circuitry must be switched off before changing any wiring.
✓ It is important that all connections be made correctly and that they are carefully checked before switching on the circuit. This is especially true of the power supply connections for the ICs (Usually the corner pins p14/15 = Vcc, p7/8 = Gnd).
✓ Before changing the circuit, discharge any static electricity by touching an earth connection on the baseboard (bottom or top row of pins).
✓ ICs should be stored pressed into anti-static foam when not in use.
✓ The board should be stored in the anti-static bag when being carried.
✗ The plug-in modules should not be moved.
Failure to observe these precautions may easily result in damage to the hardware!

How to bend IC leads
It is necessary to bend the leads of the ICs before trying to insert them into the prototyping board. Use the method shown below or use the pin straighteners available in the lab sessions.

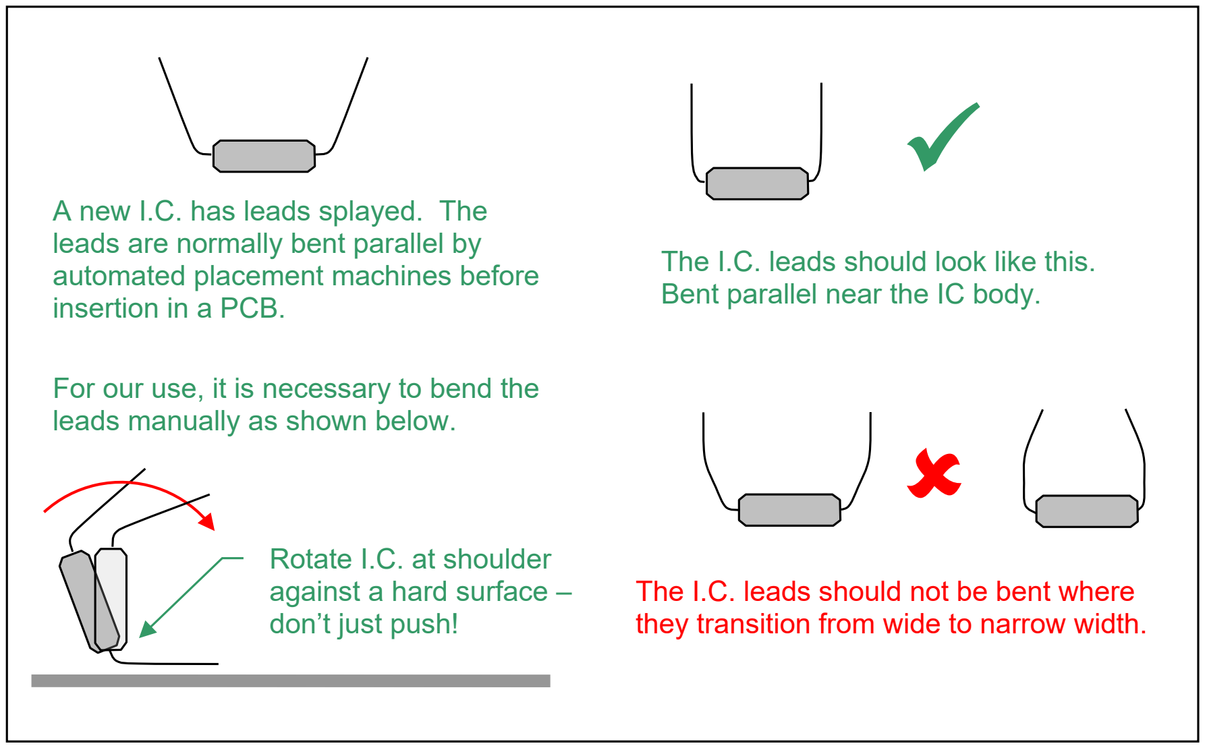
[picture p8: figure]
Rotate I.C. at shoulder against a hard surface – don’t just push!; A new I.C. has leads splayed. The leads are normally bent parallel by automated placement machines before insertion in a PCB.; The I.C. leads should look like this. Bent parallel near the IC body.; The I.C. leads should not be bent where; leads manually as shown below.

they transition from wide to narrow width.

For our use, it is necessary to bend the

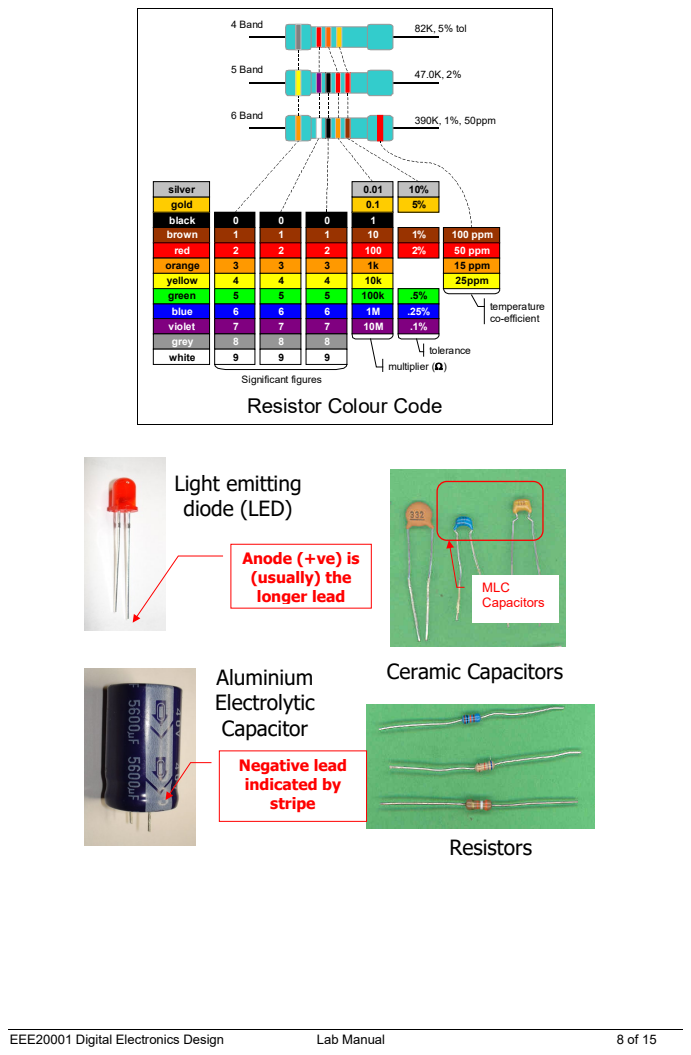
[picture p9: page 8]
4 Band; 5 Band; 6 Band; 82K, 5% tol; 390K, 1%, 50ppm; multiplier (Ω); tolerance; temperature co-efficient; gold; silver; Ceramic Capacitors; Resistors; Negative lead indicated by stripe; Light emitting diode (LED); Aluminium Electrolytic Capacitor; MLC Capacitors

black | 0 | 0 | 0 | 1
brown | 1 | 1 | 1 | 10 | 1% | 100 ppm
red | 2 | 2 | 2 | 100 | 2% | 50 ppm
orange | 3 | 3 | 3 | 1k | | 15 ppm
yellow | 4 | 4 | 4 | 10k | | 25ppm
green | 5 | 5 | 5 | 100k | .5%
blue | 6 | 6 | 6 | 1M | .25%
violet | 7 | 7 | 7 | 10M | .1%
grey | 8 | 8 | 8
white | 9 | 9 | 9

Significant figures
Resistor Colour Code

Anode (+ve) is
(usually) the
longer lead

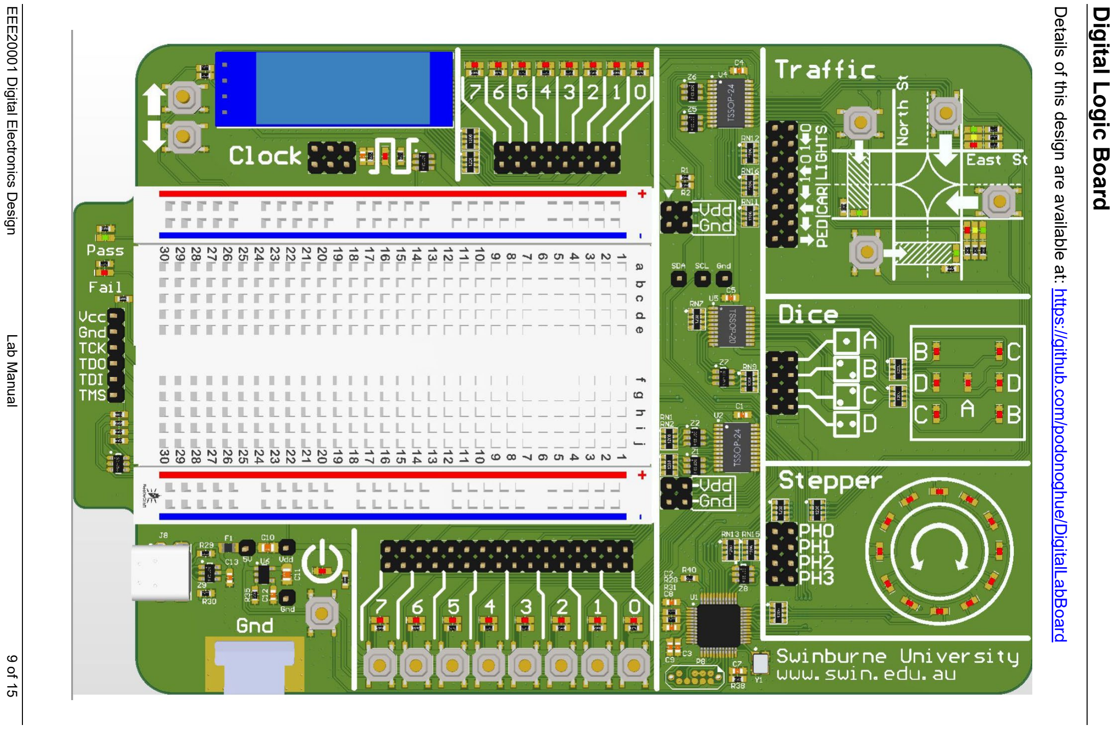
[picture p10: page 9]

EEE20001 Digital Electronics Design Lab Manual 9 of 15

Details of

## Digital Logic Board

this design are available at: https://github.com/podonoghue/DigitalLabBoard

Power and Ground clip location

### The power for the board is obtained through a USB-C connector. A suitable USB

lead with right-angle connector is provided.

### The on-board regulator reduces this to

3.3V to power the board.

### There is soft power button that controls

the power to the breadboard.

### The power will also switch off if the supply

is overloaded.

### Any settings, such as latched buttons or clock frequency are preserved when the

soft power button is used.

### A metal clip provides a convenient location

for the ground clip of oscilloscope leads.

CPLD Programming interface (JTAG)

### The programming interface allow the design to be downloaded to the CPLD from a PC via the USB

interface.
The required software is available on Canvas.

### The two LEDs indicate the outcome of the last

programming action.

### Pass => Successful Fail => Failed – check the status in the programming software for more information. The most common error is likely to be a wiring mistake

on the JTAG leads or the no power to the CPLD. The Red LED will also flash during programming.

Ground location for
oscilloscope leads

Power and programming
connection

Power
switch

## The board should be soft powered-off when making

wiring changes or moving the programming cable.

The outputs have 470 Ω series resistors for protection.

Switch Module
This provides 8 de-bounced switches that can be used as inputs to your circuit. Each output is connected to a group of four pins (2x2) as indicated for switch 4.
Switches are momentary action but will latch high if held for ~2 seconds. Press again to release. The LED is on when the output is high.

The LED is on when the output is high. The output has a 100 Ω series resistor for protection.

Clock Module
This produces a square wave in the following frequencies:
1,2,5,10,20,50,100,200,500 Hz, and 1,2,5,10,20,50,100,200,500 kHz, and
1,2 MHz
The up/down button may be used to move between the available settings.
The clock output is connected to all six pins (2x3).

LED Module
This allows 8 signals to be monitored on 8 LEDs. Each input is connected to a pair of pins (1x2) in the central block as indicated for LED 4.
The inputs are buffered so only lightly load the input signal.
The inputs have weak pull-down resistors (~10K).

Dice Module
This provides 7 LEDs arranged in a dice pattern. Each input is connected to a pair of pins (2x1) and controls one or more LEDs as shown in the legend e.g. the B input controls two diagonal LEDs.
The inputs are buffered so only lightly load the input signal.
The inputs have weak pull-down resistors (~10K).

The LED inputs have weak pull-down resistors (~10K).

Motor Module
Provides 12 LEDs arranged in a circle to represent the positions of a stepper motor.
The 4 inputs to the board represent the 4 phases of the stepper motor coil drivers. The illuminated LED will move clockwise/anti-clockwise when the appropriate sequence is presented at these inputs.
Each input is connected to a pair of pins (2x1) in the central block
The inputs are buffered so only lightly load the input signal.

The inputs are buffered so only lightly load the input signal.
The inputs have weak pull-down resistors (~10K).
The outputs have 470 Ω series resistors for protection.

Traffic Intersection Module
Provides a simple simulation of a traffic intersection with the following elements:
Inputs to module (Traffic Lights + Walk light) The lights have a 2-bit input to control a set of 4 lights (Red/Amber/Green Traffic + Green Walk)
- North-South lights
- East-West lights
Input 1 0 | Lights ← ↓
0 0 | Red
0 1 | Amber
1 0 | Green
1 1 | Green + Walk
Outputs from module (Buttons)
Each car or pedestrian is represented by a de-bounced button with an individual output reflecting its value.
- Car travelling North to South (CAR↓)
- Car travelling East to West (CAR←)
- Pedestrian crossing North to South (PED↓)
- Pedestrian crossing West to East (PED→)

Inputs to Lights

Outputs from car and pedestrian buttons

## CPLD Module

Details of this design are available at: https://github.com/podonoghue/CPLD_Breakout

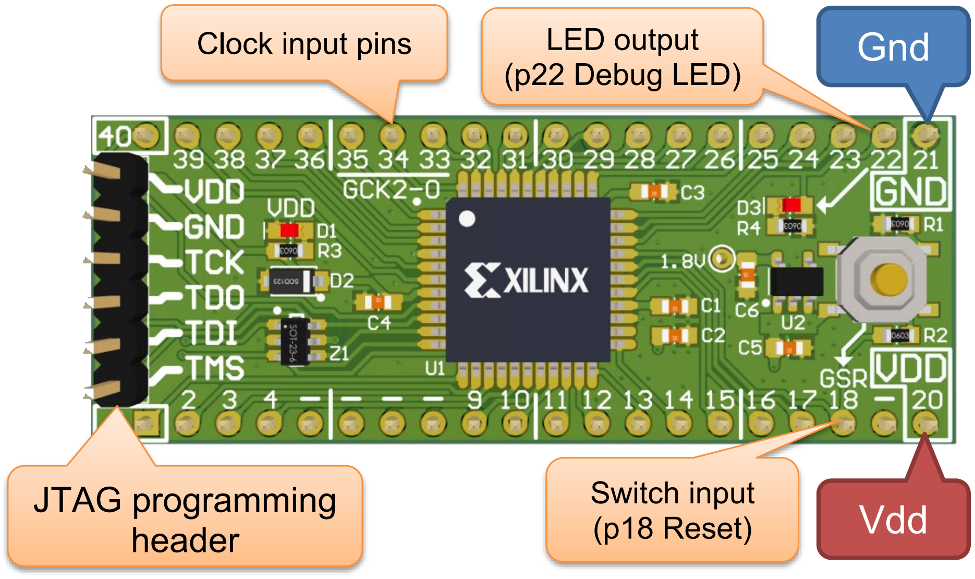
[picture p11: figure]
Gnd; Vdd JTAG programming header; Switch input (p18 Reset); LED output (p22 Debug LED); Clock input pins

This module provides a convenient interface to a Xilinx XC2C64A CPLD. This device is large enough to implement all the functions constructed in the laboratory program but cheap enough that we don’t cry too much when you blow them up 😊😊.
The inputs and outputs of the CPLD are NOT protected so it is important to check your wiring and be aware of static electricity. Do not alter the circuit while it is powered.
Most of the pins connect directly to the prototyping board and then allow connection to the I/O devices being used, for example the LEDs, switches and the clock board. Refer to the ‘UCF’ file (C-MOD.ucf) provided with the VHDL project material for actual CPLD pin numbers. Use of the UCF file is described in detail on Canvas. (https://swinburne.instructure.com/courses/23349/pages/base-ucf-file-for-cpld?module_item_id=1232904)
In addition, there is a row of pins used to connect to the CPLD programming interface. The desired hardware function would be designed using the Xilinx ISE (https://swinburne.instructure.com/courses/23349/pages/xilinx-ise-software-download-and-installation?module_item_id=1232916) software running on a PC and then downloaded to the device using this interface. This is a non-volatile device so once programmed with the desired functionality it will be retained even if power is disconnected.

### Simplified CPLD Module Schematic

Clock 35

Vdd

20

Gnd
21

General I/O Pins
1-4, 9-17, 22-34, 36-40 Reset 18

EEE20001 Digital Electronics Design Lab Manual 14 of 15

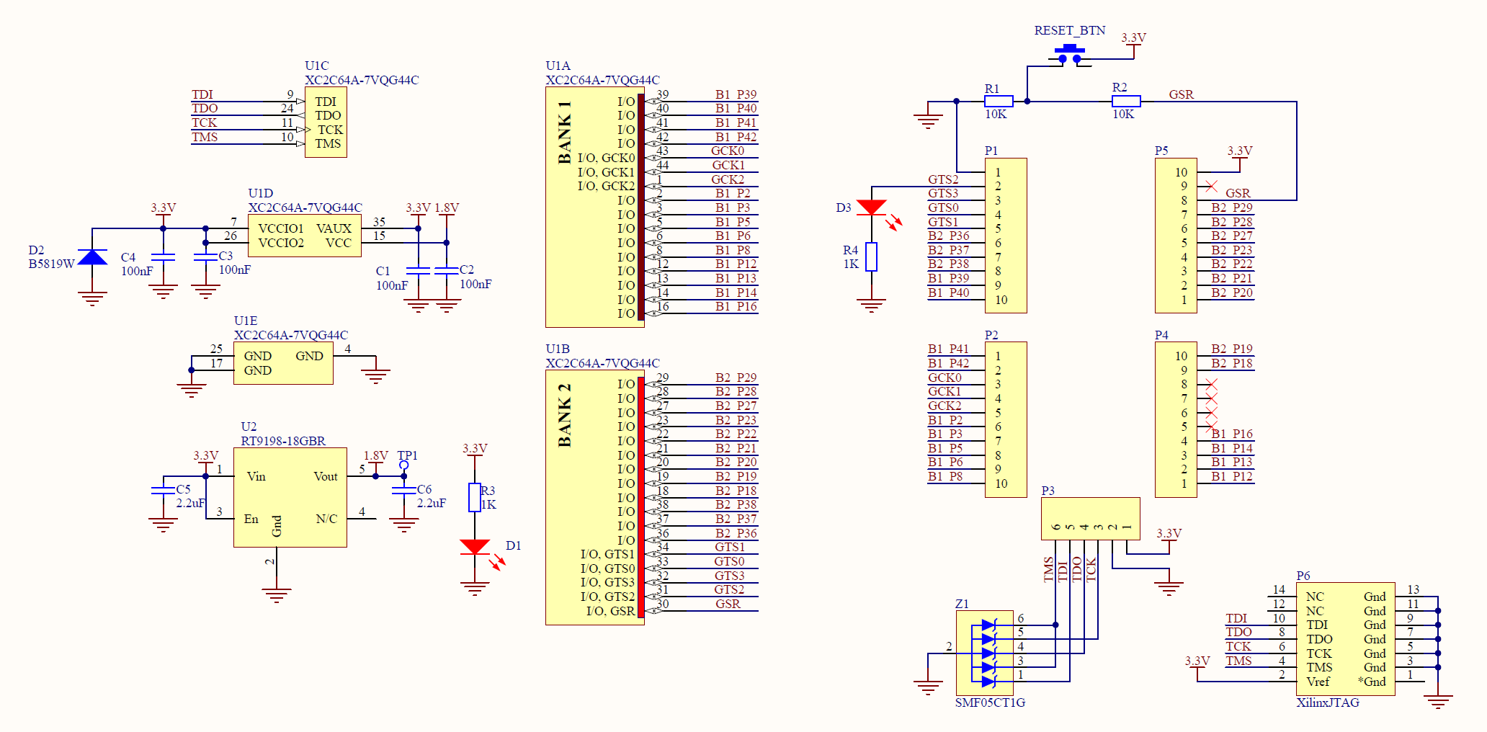
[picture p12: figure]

Integrated Circuit Pin-outs

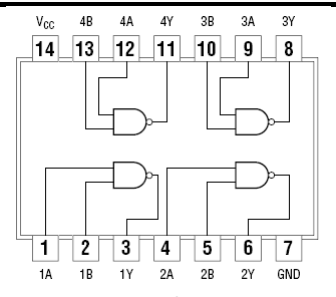
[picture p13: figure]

74HC00
Quad NAND gate

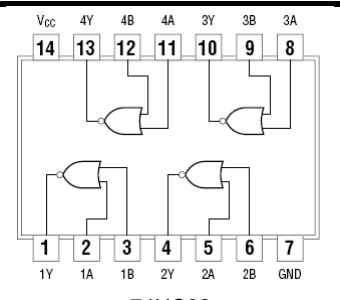
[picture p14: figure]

74HC02
Quad NOR gate

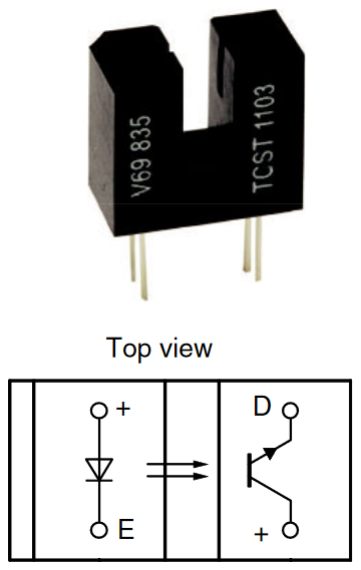
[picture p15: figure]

VISHAY TCST1103
Photo-interrupter

Detailed information about the various ICs is available on Canvas in the Laboratory area.

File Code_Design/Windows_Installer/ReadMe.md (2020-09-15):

# CPLD Programmer Installer for Windows

This is a WIX project to create a Windows installer

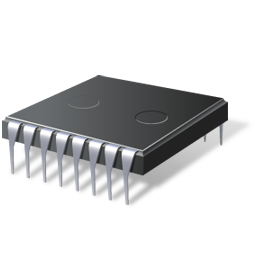
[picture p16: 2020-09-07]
Code_Design/Linux_Installer/Image.ref/usr/share/pixmaps/kinetisbootloader.png

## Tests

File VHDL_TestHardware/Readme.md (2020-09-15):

# Hardware test programs for CPLD breakout

- cpld_simple - Simply connects the Reset pin to the LED pin
- cpld_tester - Toggles all pins (required clock)

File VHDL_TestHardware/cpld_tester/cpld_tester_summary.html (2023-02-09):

cpld_tester Project Status (02/03/2023 - 17:48:29)
Project File: | cpld_tester.xise | Parser Errors: | No Errors
Module Name: | cpld_tester | Implementation State: | Fitted
Target Device: | xc2c64a-5VQ44 | Errors: | No Errors
Product Version: | ISE 14.7 | Warnings: | No Warnings
Design Goal: | Balanced | Routing Results:
Design Strategy: | Xilinx Default (unlocked) | Timing Constraints:
Environment: | System Settings | Final Timing Score:

Detailed Reports | | | | | | [-]
Report Name | Status | Generated | Errors | Warnings | Infos
Synthesis Report | Current | Sat Feb 4 18:11:25 2023 | 0 | 0 | 0
Translation Report | Current | Sat Feb 4 18:11:27 2023 | 0 | 0 | 0
CPLD Fitter Report (Text) | Current | Sat Feb 4 18:11:29 2023 | 0 | 1 Warning (1 new) | 1 Info (1 new)
Power Report

Secondary Reports | | | [-]
Report Name | Status | Generated
ISIM Simulator Log | Out of Date | Fri Feb 3 22:57:11 2023
Post-Fit Simulation Model Report

Date Generated: 02/05/2023 - 10:34:35

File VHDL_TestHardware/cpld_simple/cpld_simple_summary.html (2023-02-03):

cpld_simple Project Status (02/03/2023 - 17:46:22)
Project File: | cpld_simple.xise | Parser Errors: | No Errors
Module Name: | cpld_simple | Implementation State: | Synthesized
Target Device: | xc2c64a-5VQ44 | Errors: | No Errors
Product Version: | ISE 14.7 | Warnings: | No Warnings
Design Goal: | Balanced | Routing Results:
Design Strategy: | Xilinx Default (unlocked) | Timing Constraints:
Environment: | System Settings | Final Timing Score:

Detailed Reports | | | | | | [-]
Report Name | Status | Generated | Errors | Warnings | Infos
Synthesis Report | Current | Fri Feb 3 17:46:22 2023 | 0 | 0 | 0
Translation Report
CPLD Fitter Report (Text)
Power Report

Secondary Reports | | | [-]
Report Name | Status | Generated
Post-Fit Simulation Model Report

Date Generated: 02/03/2023 - 17:46:22

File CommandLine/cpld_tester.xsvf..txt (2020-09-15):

// Created from : 'cpld_tester.xsvf'

#define BYTES32(x) (0xFF&((x)>>24)),(0xFF&((x)>>16)),(0xFF&((x)>>8)),(0xFF&(x))
   
   static constexpr uint8_t Ex_Idle        = 0x00;
   static constexpr uint8_t Ex_DR_Pause    = 0x01;
   static constexpr uint8_t Ex_IR_Pause    = 0x01;
   static constexpr uint8_t IDCODE_COMMAND = 0x01;
   static constexpr uint8_t BYPASS_COMMAND = 0xFF;
   static constexpr uint8_t ENABLE_COMMAND = 0xE8;
   static constexpr uint8_t ERASE_COMMAND  = 0xED;
   static constexpr uint8_t INIT_COMMAND   = 0xF0;
   static constexpr uint8_t CONLD_COMMAND  = 0xC0;
   static constexpr uint8_t INIT_COMMAND   = 0xED;
   static constexpr uint8_t VERIFY_COMMAND = 0xEE;
   
   static const uint8_t xsvf_data[] = {
   /* Reset           */ XREPEAT, 0,
   /* Reset           */ XENDIR, Ex_Idle, // Idle
   /* Reset           */ XENDDR, Ex_Idle, // Idle
   /* Reset           */ XSTATE, Reset,
   /* Reset           */ XSTATE, Idle,
   /* Idle            */ XSIR, 8, // -DR_Select-IR_Select-IR_Capture-IR_Shift-IR_Update-Idle
   /* tdi_value     8:*/ 0x01, 
   /* Idle            */ XSDRSIZE, BYTES32(32),
   /* Idle            */ XTDOMASK, // (32 bits)
   /* tdo_mask     32:*/ 0x0F, 0xFF, 0x8F, 0xFF, 
   /* Idle            */ XRUNTEST, BYTES32(0) // cycle/ms
   /* Idle            */ XSDRTDO, // (32 bits)-DR_Select-DR_Capture-DR_Shift-DR_Update-Idle
   /* tdi_value    32:*/ 0x00, 0x00, 0x00, 0x00, 
   /* tdo_value    32:*/ 0xF6, 0xE5, 0xF0, 0x93, 
   /* Idle            */ XSIR, 8, // -DR_Select-IR_Select-IR_Capture-IR_Shift-IR_Update-Idle
   /* tdi_value     8:*/ 0xFF, 
   /* Idle            */ XSIR, 8, // -DR_Select-IR_Select-IR_Capture-IR_Shift-IR_Update-Idle
   /* tdi_value     8:*/ 0x01, 
   /* Idle            */ XSDRTDO, // (32 bits)-DR_Select-DR_Capture-DR_Shift-DR_Update-Idle
   /* tdi_value    32:*/ 0x00, 0x00, 0x00, 0x00, 
   /* tdo_value    32:*/ 0xF6, 0xE5, 0xF0, 0x93, 
   /* Idle            */ XSIR, 8, // -DR_Select-IR_Select-IR_Capture-IR_Shift-IR_Update-Idle
   /* tdi_value     8:*/ 0xFF, 
   /* Idle            */ XSIR, 8, // -DR_Select-IR_Select-IR_Capture-IR_Shift-IR_Update-Idle
   /* tdi_value     8:*/ 0x01, 
   /* Idle            */ XSDRTDO, // (32 bits)-DR_Select-DR_Capture-DR_Shift-DR_Update-Idle
   /* tdi_value    32:*/ 0x00, 0x00, 0x00, 0x00, 
   /* tdo_value    32:*/ 0xF6, 0xE5, 0xF0, 0x93, 
   /* Idle            */ XREPEAT, 0,
   /* Idle            */ XREPEAT, 0,
   /* Idle            */ XENDIR, Ex_Idle, // Idle
   /* Idle            */ XENDDR, Ex_Idle, // Idle
   /* Idle            */ XSTATE, Reset,
   /* Reset           */ XSTATE, Idle,
   /* Idle            */ XSIR, 8, // -DR_Select-IR_Select-IR_Capture-IR_Shift-IR_Update-Idle
   /* tdi_value     8:*/ 0xFF, 
   /* Idle            */ XSDRSIZE, BYTES32(1),
   /* Idle            */ XTDOMASK, // (1 bits)
   /* tdo_mask      1:*/ 0x00, 
   /* Idle            */ XRUNTEST, BYTES32(0) // cycle/ms
   /* Idle            */ XSDRTDO, // (1 bits)-DR_Select-DR_Capture-DR_Shift-DR_Update-Idle
   /* tdi_value     1:*/ 0x00, 
   /* tdo_value     1:*/ 0x00, 
   /* Idle            */ XSIR, 8, // -DR_Select-IR_Select-IR_Capture-IR_Shift-IR_Update-Idle
   /* tdi_value     8:*/ 0x01, 
   /* Idle            */ XSDRSIZE, BYTES32(32),
   /* Idle            */ XTDOMASK, // (32 bits)
   /* tdo_mask     32:*/ 0x0F, 0xFF, 0x8F, 0xFF, 
   /* Idle            */ XSDRTDO, // (32 bits)-DR_Select-DR_Capture-DR_Shift-DR_Update-Idle
   /* tdi_value    32:*/ 0x00, 0x00, 0x00, 0x00, 
   /* tdo_value    32:*/ 0xF6, 0xE5, 0xF0, 0x93, 
   /* Idle            */ XSIR, 8, // -DR_Select-IR_Select-IR_Capture-IR_Shift-IR_Update-Idle
   /* tdi_value     8:*/ 0xFF, 
   /* Idle            */ XSIR, 8, // -DR_Select-IR_Select-IR_Capture-IR_Shift-IR_Update-Idle
   /* tdi_value     8:*/ 0x01, 
   /* Idle            */ XSDRTDO, // (32 bits)-DR_Select-DR_Capture-DR_Shift-DR_Update-Idle
   /* tdi_value    32:*/ 0x00, 0x00, 0x00, 0x00, 
   /* tdo_value    32:*/ 0xF6, 0xE5, 0xF0, 0x93, 
   /* Idle            */ XSIR, 8, // -DR_Select-IR_Select-IR_Capture-IR_Shift-IR_Update-Idle
   /* tdi_value     8:*/ 0xFF, 
   /* Idle            */ XSIR, 8, // -DR_Select-IR_Select-IR_Capture-IR_Shift-IR_Update-Idle
   /* tdi_value     8:*/ 0xE8, 
   /* Idle            */ XENDIR, Ex_IR_Pause, // IR_Pause
   /* Idle            */ XSIR, 8, // -DR_Select-IR_Select-IR_Capture-IR_Shift-IR_Pause
   /* tdi_value     8:*/ 0xED, 
   /* IR_Pause        */ XENDIR, Ex_Idle, // Idle
   /* IR_Pause        */ XSTATE, IR_Exit2,
   /* IR_Exit2        */ XSTATE, IR_Update,
   /* IR_Update       */ XSTATE, DR_Select,
   /* DR_Select       */ XSTATE, DR_Capture,
   /* DR_Capture      */ XSTATE, DR_Exit1,
   /* DR_Exit1        */ XSTATE, DR_Pause,
   /* DR_Pause        */ XWAIT, DR_Pause, DR_Pause, 20 // 
   /* DR_Pause        */ XSTATE, DR_Exit2,
   /* DR_Exit2        */ XSTATE, DR_Update,
   /* DR_Update       */ XSTATE, Idle,
   /* Idle            */ XWAIT, Idle, Idle, 100000 // 
   /* Idle            */ XSTATE, DR_Select,
   /* DR_Select       */ XSTATE, DR_Capture,
   /* DR_Capture      */ XSTATE, DR_Exit1,
   /* DR_Exit1        */ XSTATE, DR_Pause,
   /* DR_Pause        */ XWAIT, DR_Pause, DR_Pause, 5000 // 
   /* DR_Pause        */ XWAIT, Idle, Idle, 1 // -DR_Exit2-DR_Update-Idle
   /* Idle            */ XENDIR, Ex_IR_Pause, // IR_Pause
   /* Idle            */ XSIR, 8, // -DR_Select-IR_Select-IR_Capture-IR_Shift-IR_Pause
   /* tdi_value     8:*/ 0xF0, 
   /* IR_Pause        */ XSTATE, IR_Exit2,
   /* IR_Exit2        */ XSTATE, IR_Update,
   /* IR_Update       */ XSTATE, Idle,
   /* Idle            */ XWAIT, Idle, Idle, 20 // 
   /* Idle            */ XENDIR, Ex_IR_Pause, // IR_Pause
   /* Idle            */ XSIR, 8, // -DR_Select-IR_Select-IR_Capture-IR_Shift-IR_Pause
   /* tdi_value     8:*/ 0xF0, 
   /* IR_Pause        */ XSTATE, IR_Exit2,
   /* IR_Exit2        */ XSTATE, IR_Update,
   /* IR_Update       */ XSTATE, DR_Select,
   /* DR_Select       */ XSTATE, DR_Capture,
   /* DR_Capture      */ XSTATE, DR_Exit1,
   /* DR_Exit1        */ XSTATE, DR_Update,
   /* DR_Update       */ XSTATE, Idle,
   /* Idle            */ XWAIT, Idle, Idle, 800 // 
   /* Idle            */ XENDIR, Ex_Idle, // Idle
   /* Idle            */ XSIR, 8, // -DR_Select-IR_Select-IR_Capture-IR_Shift-IR_Update-Idle
   /* tdi_value     8:*/ 0xC0, 
   /* Idle            */ XWAIT, Idle, Idle, 100 // 
   /* Idle            */ XSIR, 8, // -DR_Select-IR_Select-IR_Capture-IR_Shift-IR_Update-Idle
   /* tdi_value     8:*/ 0xC0, 
   /* Idle            */ XWAIT, Idle, Idle, 100 // 
   /* Idle            */ XSIR, 8, // -DR_Select-IR_Select-IR_Capture-IR_Shift-IR_Update-Idle
   /* tdi_value     8:*/ 0xE8, 
   /* Idle            */ XENDIR, Ex_IR_Pause, // IR_Pause
   /* Idle            */ XSIR, 8, // -DR_Select-IR_Select-IR_Capture-IR_Shift-IR_Pause
   /* tdi_value     8:*/ 0xEA, 
   /* IR_Pause        */ XSDRSIZE, BYTES32(281),
   /* IR_Pause        */ XTDOMASK, // (281 bits)
   /* tdo_mask    281:*/ 0x00, 0x00, 0x00, 0x00, 0x00, 0x00, 0x00, 0x00, 
   /* tdo_mask    224:*/ 0x00, 0x00, 0x00, 0x00, 0x00, 0x00, 0x00, 0x00, 
   /* tdo_mask    160:*/ 0x00, 0x00, 0x00, 0x00, 0x00, 0x00, 0x00, 0x00, 
   /* tdo_mask     96:*/ 0x00, 0x00, 0x00, 0x00, 0x00, 0x00, 0x00, 0x00, 
   /* tdo_mask     32:*/ 0x00, 0x00, 0x00, 0x00, 
   /* IR_Pause        */ XSDRTDO, // (281 bits)-IR_Exit2-IR_Update-DR_Select-DR_Capture-DR_Shift-DR_Update-Idle
   /* tdi_value   281:*/ 0x00, 0x03, 0xC1, 0xFF, 0xFF, 0xFF, 0xFF, 0xFF, 
   /* tdi_value   224:*/ 0xFF, 0xFF, 0xFF, 0xFF, 0xFF, 0xFF, 0xFF, 0xFF, 
   /* tdi_value   160:*/ 0xFF, 0xFF, 0xFF, 0xFF, 0xFF, 0xFF, 0xFF, 0xFF, 
   /* tdi_value    96:*/ 0xFF, 0xFF, 0xFF, 0xFF, 0xFF, 0xFF, 0xFF, 0xFF, 
   /* tdi_value    32:*/ 0xFF, 0xFF, 0xFE, 0x0F, 
   /* tdo_value   281:*/ 0x00, 0x00, 0x00, 0x00, 0x00, 0x00, 0x00, 0x00, 
   /* tdo_value   224:*/ 0x00, 0x00, 0x00, 0x00, 0x00, 0x00, 0x00, 0x00, 
   /* tdo_value   160:*/ 0x00, 0x00, 0x00, 0x00, 0x00, 0x00, 0x00, 0x00, 
   /* tdo_value    96:*/ 0x00, 0x00, 0x00, 0x00, 0x00, 0x00, 0x00, 0x00, 
   /* tdo_value    32:*/ 0x00, 0x00, 0x00, 0x00, 
   /* Idle            */ XENDIR, Ex_Idle, // Idle
   /* Idle            */ XWAIT, Idle, Idle, 10000 // 
   /* Idle            */ XSDRTDO, // (281 bits)-DR_Select-DR_Capture-DR_Shift-DR_Update-Idle
   /* tdi_value   281:*/ 0x01, 0x03, 0xF9, 0xFF, 0xFF, 0xFF, 0xFF, 0xFF, 
   /* tdi_value   224:*/ 0xFF, 0xFF, 0xFF, 0xFF, 0xFF, 0x7F, 0xFF, 0xFF, 
   /* tdi_value   160:*/ 0xFF, 0xBB, 0xFE, 0xFF, 0xFF, 0xFF, 0xFF, 0xFF, 
   /* tdi_value    96:*/ 0xFF, 0xFF, 0xFF, 0xFF, 0xFF, 0xFF, 0xFF, 0xFF, 
   /* tdi_value    32:*/ 0xFF, 0xFF, 0xFE, 0x7F, 
   /* tdo_value   281:*/ 0x00, 0x00, 0x00, 0x00, 0x00, 0x00, 0x00, 0x00, 
   /* tdo_value   224:*/ 0x00, 0x00, 0x00, 0x00, 0x00, 0x00, 0x00, 0x00, 
   /* tdo_value   160:*/ 0x00, 0x00, 0x00, 0x00, 0x00, 0x00, 0x00, 0x00, 
   /* tdo_value    96:*/ 0x00, 0x00, 0x00, 0x00, 0x00, 0x00, 0x00, 0x00, 
   /* tdo_value    32:*/ 0x00, 0x00, 0x00, 0x00, 
   /* Idle            */ XWAIT, Idle, Idle, 10000 // 
   /* Idle            */ XSDRTDO, // (281 bits)-DR_Select-DR_Capture-DR_Shift-DR_Update-Idle
   /* tdi_value   281:*/ 0x01, 0x80, 0xF9, 0xFF, 0xFF, 0xFF, 0xFF, 0xFF, 
   /* tdi_value   224:*/ 0xFF, 0xFF, 0xFF, 0xFF, 0xFF, 0xFF, 0xFF, 0xFF, 
   /* tdi_value   160:*/ 0xFF, 0xFF, 0xFF, 0xFF, 0xFF, 0xFF, 0xFF, 0xFF, 
   /* tdi_value    96:*/ 0xFF, 0xFF, 0xFF, 0xFF, 0xFF, 0xFF, 0xFF, 0xFF, 
   /* tdi_value    32:*/ 0xFF, 0xFF, 0xFE, 0x7C, 
   /* tdo_value   281:*/ 0x00, 0x00, 0x00, 0x00, 0x00, 0x00, 0x00, 0x00, 
   /* tdo_value   224:*/ 0x00, 0x00, 0x00, 0x00, 0x00, 0x00, 0x00, 0x00, 
   /* tdo_value   160:*/ 0x00, 0x00, 0x00, 0x00, 0x00, 0x00, 0x00, 0x00, 
   /* tdo_value    96:*/ 0x00, 0x00, 0x00, 0x00, 0x00, 0x00, 0x00, 0x00, 
   /* tdo_value    32:*/ 0x00, 0x00, 0x00, 0x00, 
   /* Idle            */ XWAIT, Idle, Idle, 10000 // 
   /* Idle            */ XSDRTDO, // (281 bits)-DR_Select-DR_Capture-DR_Shift-DR_Update-Idle
   /* tdi_value   281:*/ 0x00, 0x83, 0xC1, 0xFF, 0xFF, 0xFF, 0xFF, 0xFF, 
   /* tdi_value   224:*/ 0xFF, 0xFF, 0xFF, 0xFF, 0xFF, 0xFF, 0xFF, 0xFF, 
   /* tdi_value   160:*/ 0xFF, 0xFF, 0xFF, 0xFF, 0xFF, 0xFF, 0xFF, 0xFF, 
   /* tdi_value    96:*/ 0xFF, 0xFF, 0xFF, 0xFF, 0xFF, 0xFF, 0xFF, 0xFF, 
   /* tdi_value    32:*/ 0xFF, 0xFF, 0xFE, 0x0F, 
   /* tdo_value   281:*/ 0x00, 0x00, 0x00, 0x00, 0x00, 0x00, 0x00, 0x00, 
   /* tdo_value   224:*/ 0x00, 0x00, 0x00, 0x00, 0x00, 0x00, 0x00, 0x00, 
   /* tdo_value   160:*/ 0x00, 0x00, 0x00, 0x00, 0x00, 0x00, 0x00, 0x00, 
   /* tdo_value    96:*/ 0x00, 0x00, 0x00, 0x00, 0x00, 0x00, 0x00, 0x00, 
   /* tdo_value    32:*/ 0x00, 0x00, 0x00, 0x00, 
   /* Idle            */ XWAIT, Idle, Idle, 10000 // 
   /* Idle            */ XSDRTDO, // (281 bits)-DR_Select-DR_Capture-DR_Shift-DR_Update-Idle
   /* tdi_value   281:*/ 0x00, 0xC3, 0xF9, 0xFF, 0xFF, 0xFF, 0xFF, 0xFF, 
   /* tdi_value   224:*/ 0xFF, 0xFF, 0xFF, 0xFF, 0xFF, 0xFF, 0xFF, 0xFF, 
   /* tdi_value   160:*/ 0xFF, 0xFF, 0xFF, 0xFF, 0xFF, 0xFF, 0xFF, 0xFF, 
   /* tdi_value    96:*/ 0xFF, 0xFF, 0xFF, 0xFF, 0xFF, 0xFF, 0xFF, 0xFF, 
   /* tdi_value    32:*/ 0xFF, 0xFF, 0xFE, 0x7F, 
   /* tdo_value   281:*/ 0x00, 0x00, 0x00, 0x00, 0x00, 0x00, 0x00, 0x00, 
   /* tdo_value   224:*/ 0x00, 0x00, 0x00, 0x00, 0x00, 0x00, 0x00, 0x00, 
   /* tdo_value   160:*/ 0x00, 0x00, 0x00, 0x00, 0x00, 0x00, 0x00, 0x00, 
   /* tdo_value    96:*/ 0x00, 0x00, 0x00, 0x00, 0x00, 0x00, 0x00, 0x00, 
   /* tdo_value    32:*/ 0x00, 0x00, 0x00, 0x00, 
   /* Idle            */ XWAIT, Idle, Idle, 10000 // 
   /* Idle            */ XSDRTDO, // (281 bits)-DR_Select-DR_Capture-DR_Shift-DR_Update-Idle
   /* tdi_value   281:*/ 0x01, 0xC0, 0xF9, 0xFF, 0xFF, 0xFF, 0xFF, 0xFF, 
   /* tdi_value   224:*/ 0xFF, 0xFF, 0xFF, 0xFF, 0xFF, 0xFF, 0xFF, 0xFF, 
   /* tdi_value   160:*/ 0xFF, 0xFF, 0xFF, 0xFF, 0xFF, 0xFF, 0xFF, 0xFF, 
   /* tdi_value    96:*/ 0xFF, 0xFF, 0xFF, 0xFF, 0xFF, 0xFF, 0xFF, 0xFF, 
   /* tdi_value    32:*/ 0xFF, 0xFF, 0xFE, 0x7C, 
   /* tdo_value   281:*/ 0x00, 0x00, 0x00, 0x00, 0x00, 0x00, 0x00, 0x00, 
   /* tdo_value   224:*/ 0x00, 0x00, 0x00, 0x00, 0x00, 0x00, 0x00, 0x00, 
   /* tdo_value   160:*/ 0x00, 0x00, 0x00, 0x00, 0x00, 0x00, 0x00, 0x00, 
   /* tdo_value    96:*/ 0x00, 0x00, 0x00, 0x00, 0x00, 0x00, 0x00, 0x00, 
   /* tdo_value    32:*/ 0x00, 0x00, 0x00, 0x00, 
   /* Idle            */ XWAIT, Idle, Idle, 10000 // 
   /* Idle            */ XSDRTDO, // (281 bits)-DR_Select-DR_Capture-DR_Shift-DR_Update-Idle
   /* tdi_value   281:*/ 0x01, 0x43, 0xC1, 0xFF, 0xFF, 0xFF, 0xFF, 0xFF, 
   /* tdi_value   224:*/ 0xFF, 0xFF, 0xFF, 0xFF, 0xFF, 0xFF, 0xFF, 0xFF, 
   /* tdi_value   160:*/ 0xFF, 0xFF, 0xFF, 0xFF, 0xFF, 0xFF, 0xFF, 0xFF, 
   /* tdi_value    96:*/ 0xFF, 0xFF, 0xFF, 0xFF, 0xFF, 0xFF, 0xFF, 0xFF, 
   /* tdi_value    32:*/ 0xFF, 0xFF, 0xFE, 0x0F, 
   /* tdo_value   281:*/ 0x00, 0x00, 0x00, 0x00, 0x00, 0x00, 0x00, 0x00, 
   /* tdo_value   224:*/ 0x00, 0x00, 0x00, 0x00, 0x00, 0x00, 0x00, 0x00, 
   /* tdo_value   160:*/ 0x00, 0x00, 0x00, 0x00, 0x00, 0x00, 0x00, 0x00, 
   /* tdo_value    96:*/ 0x00, 0x00, 0x00, 0x00, 0x00, 0x00, 0x00, 0x00, 
   /* tdo_value    32:*/ 0x00, 0x00, 0x00, 0x00, 
   /* Idle            */ XWAIT, Idle, Idle, 10000 // 
   /* Idle            */ XSDRTDO, // (281 bits)-DR_Select-DR_Capture-DR_Shift-DR_Update-Idle
   /* tdi_value   281:*/ 0x00, 0x43, 0xF9, 0xFF, 0xFF, 0xFF, 0xFF, 0xFF, 
   /* tdi_value   224:*/ 0xFF, 0xFF, 0xFF, 0xFF, 0xFF, 0xFF, 0xFF, 0xFF, 
   /* tdi_value   160:*/ 0xFF, 0xFF, 0xFF, 0xFF, 0xFF, 0xFF, 0xFF, 0xFF, 
   /* tdi_value    96:*/ 0xFF, 0xFF, 0xFF, 0xFF, 0xFF, 0xFF, 0xFF, 0xFF, 
   /* tdi_value    32:*/ 0xFF, 0xFF, 0xFE, 0x7F, 
   /* tdo_value   281:*/ 0x00, 0x00, 0x00, 0x00, 0x00, 0x00, 0x00, 0x00, 
   /* tdo_value   224:*/ 0x00, 0x00, 0x00, 0x00, 0x00, 0x00, 0x00, 0x00, 
   /* tdo_value   160:*/ 0x00, 0x00, 0x00, 0x00, 0x00, 0x00, 0x00, 0x00, 
   /* tdo_value    96:*/ 0x00, 0x00, 0x00, 0x00, 0x00, 0x00, 0x00, 0x00, 
   /* tdo_value    32:*/ 0x00, 0x00, 0x00, 0x00, 
   /* Idle            */ XWAIT, Idle, Idle, 10000 // 
   /* Idle            */ XSDRTDO, // (281 bits)-DR_Select-DR_Capture-DR_Shift-DR_Update-Idle
   /* tdi_value   281:*/ 0x00, 0x60, 0xF9, 0xFF, 0xFF, 0xFF, 0xFF, 0xFF, 
   /* tdi_value   224:*/ 0xFF, 0xFF, 0xFF, 0xFF, 0xFF, 0xFF, 0xFF, 0xFF, 
   /* tdi_value   160:*/ 0xFF, 0xFF, 0xFF, 0xFF, 0xFF, 0xFF, 0xFF, 0xFF, 
   /* tdi_value    96:*/ 0xFF, 0xFF, 0xFF, 0xFF, 0xFF, 0xFF, 0xFF, 0xFF, 
   /* tdi_value    32:*/ 0xFF, 0xFF, 0xFE, 0x7C, 
   /* tdo_value   281:*/ 0x00, 0x00, 0x00, 0x00, 0x00, 0x00, 0x00, 0x00, 
   /* tdo_value   224:*/ 0x00, 0x00, 0x00, 0x00, 0x00, 0x00, 0x00, 0x00, 
   /* tdo_value   160:*/ 0x00, 0x00, 0x00, 0x00, 0x00, 0x00, 0x00, 0x00, 
   /* tdo_value    96:*/ 0x00, 0x00, 0x00, 0x00, 0x00, 0x00, 0x00, 0x00, 
   /* tdo_value    32:*/ 0x00, 0x00, 0x00, 0x00, 
   /* Idle            */ XWAIT, Idle, Idle, 10000 // 
   /* Idle            */ XSDRTDO, // (281 bits)-DR_Select-DR_Capture-DR_Shift-DR_Update-Idle
   /* tdi_value   281:*/ 0x01, 0x63, 0xC1, 0xFF, 0xFF, 0xFF, 0xFF, 0xFF, 
   /* tdi_value   224:*/ 0xFF, 0xFF, 0xFF, 0xFF, 0xFF, 0xFF, 0xFF, 0xFF, 
   /* tdi_value   160:*/ 0xFF, 0xFF, 0xFF, 0xFF, 0xFF, 0xFF, 0xFF, 0xFF, 
   /* tdi_value    96:*/ 0xFF, 0xFF, 0xFF, 0xFF, 0xFF, 0xFF, 0xFF, 0xFF, 
   /* tdi_value    32:*/ 0xFF, 0xFF, 0xFE, 0x0F, 
   /* tdo_value   281:*/ 0x00, 0x00, 0x00, 0x00, 0x00, 0x00, 0x00, 0x00, 
   /* tdo_value   224:*/ 0x00, 0x00, 0x00, 0x00, 0x00, 0x00, 0x00, 0x00, 
   /* tdo_value   160:*/ 0x00, 0x00, 0x00, 0x00, 0x00, 0x00, 0x00, 0x00, 
   /* tdo_value    96:*/ 0x00, 0x00, 0x00, 0x00, 0x00, 0x00, 0x00, 0x00, 
   /* tdo_value    32:*/ 0x00, 0x00, 0x00, 0x00, 
   /* Idle            */ XWAIT, Idle, Idle, 10000 // 
   /* Idle            */ XSDRTDO, // (281 bits)-DR_Select-DR_Capture-DR_Shift-DR_Update-Idle
   /* tdi_value   281:*/ 0x01, 0xE3, 0xF9, 0xFF, 0xFF, 0xFF, 0xFF, 0xFF, 
   /* tdi_value   224:*/ 0xFF, 0xFF, 0xFF, 0xFF, 0xFF, 0xFF, 0xFF, 0xFF, 
   /* tdi_value   160:*/ 0xFF, 0xFF, 0xFF, 0xFF, 0xFF, 0xFF, 0xFF, 0xFF, 
   /* tdi_value    96:*/ 0xFF, 0xFF, 0xFF, 0xFF, 0xFF, 0xFF, 0xFF, 0xFF, 
   /* tdi_value    32:*/ 0xFF, 0xFF, 0xFE, 0x7F, 
   /* tdo_value   281:*/ 0x00, 0x00, 0x00, 0x00, 0x00, 0x00, 0x00, 0x00, 
   /* tdo_value   224:*/ 0x00, 0x00, 0x00, 0x00, 0x00, 0x00, 0x00, 0x00, 
   /* tdo_value   160:*/ 0x00, 0x00, 0x00, 0x00, 0x00, 0x00, 0x00, 0x00, 
   /* tdo_value    96:*/ 0x00, 0x00, 0x00, 0x00, 0x00, 0x00, 0x00, 0x00, 
   /* tdo_value    32:*/ 0x00, 0x00, 0x00, 0x00, 
   /* Idle            */ XWAIT, Idle, Idle, 10000 // 
   /* Idle            */ XSDRTDO, // (281 bits)-DR_Select-DR_Capture-DR_Shift-DR_Update-Idle
   /* tdi_value   281:*/ 0x00, 0xE0, 0xF9, 0xFF, 0xFF, 0xFF, 0xFF, 0xFF, 
   /* tdi_value   224:*/ 0xFF, 0xFF, 0xFF, 0xFF, 0xFF, 0xFF, 0xFF, 0xFF, 
   /* tdi_value   160:*/ 0xFF, 0xFF, 0xFF, 0xFF, 0xFF, 0xFF, 0xFF, 0xFF, 
   /* tdi_value    96:*/ 0xFF, 0xFF, 0xFF, 0xFF, 0xFF, 0xFF, 0xFF, 0xFF, 
   /* tdi_value    32:*/ 0xFF, 0xFF, 0xFE, 0x7C, 
   /* tdo_value   281:*/ 0x00, 0x00, 0x00, 0x00, 0x00, 0x00, 0x00, 0x00, 
   /* tdo_value   224:*/ 0x00, 0x00, 0x00, 0x00, 0x00, 0x00, 0x00, 0x00, 
   /* tdo_value   160:*/ 0x00, 0x00, 0x00, 0x00, 0x00, 0x00, 0x00, 0x00, 
   /* tdo_value    96:*/ 0x00, 0x00, 0x00, 0x00, 0x00, 0x00, 0x00, 0x00, 
   /* tdo_value    32:*/ 0x00, 0x00, 0x00, 0x00, 
   /* Idle            */ XWAIT, Idle, Idle, 10000 // 
   /* Idle            */ XSDRTDO, // (281 bits)-DR_Select-DR_Capture-DR_Shift-DR_Update-Idle
   /* tdi_value   281:*/ 0x00, 0xA3, 0xC1, 0xFF, 0xFF, 0xFF, 0xFF, 0xFF, 
   /* tdi_value   224:*/ 0xFF, 0xFF, 0xFF, 0xFF, 0xFF, 0xFF, 0xFF, 0xFF, 
   /* tdi_value   160:*/ 0xFF, 0xFF, 0xFF, 0xFF, 0xFF, 0xFF, 0xFF, 0xFF, 
   /* tdi_value    96:*/ 0xFF, 0xFF, 0xFF, 0xFF, 0xFF, 0xFF, 0xFF, 0xFF, 
   /* tdi_value    32:*/ 0xFF, 0xFF, 0xFE, 0x0F, 
   /* tdo_value   281:*/ 0x00, 0x00, 0x00, 0x00, 0x00, 0x00, 0x00, 0x00, 
   /* tdo_value   224:*/ 0x00, 0x00, 0x00, 0x00, 0x00, 0x00, 0x00, 0x00, 
   /* tdo_value   160:*/ 0x00, 0x00, 0x00, 0x00, 0x00, 0x00, 0x00, 0x00, 
   /* tdo_value    96:*/ 0x00, 0x00, 0x00, 0x00, 0x00, 0x00, 0x00, 0x00, 
   /* tdo_value    32:*/ 0x00, 0x00, 0x00, 0x00, 
   /* Idle            */ XWAIT, Idle, Idle, 10000 // 
   /* Idle            */ XSDRTDO, // (281 bits)-DR_Select-DR_Capture-DR_Shift-DR_Update-Idle
   /* tdi_value   281:*/ 0x01, 0xA3, 0xF9, 0xFF, 0xFF, 0xFF, 0xFF, 0xFF, 
   /* tdi_value   224:*/ 0xFF, 0xFF, 0xFF, 0xFF, 0xFF, 0xFF, 0xFF, 0xFF, 
   /* tdi_value   160:*/ 0xFF, 0xFF, 0xFF, 0xFF, 0xFF, 0xFF, 0xFF, 0xFF, 
   /* tdi_value    96:*/ 0xFF, 0xFF, 0xFF, 0xFF, 0xFF, 0xFF, 0xFF, 0xFF, 
   /* tdi_value    32:*/ 0xFF, 0xFF, 0xFE, 0x7F, 
   /* tdo_value   281:*/ 0x00, 0x00, 0x00, 0x00, 0x00, 0x00, 0x00, 0x00, 
   /* tdo_value   224:*/ 0x00, 0x00, 0x00, 0x00, 0x00, 0x00, 0x00, 0x00, 
   /* tdo_value   160:*/ 0x00, 0x00, 0x00, 0x00, 0x00, 0x00, 0x00, 0x00, 
   /* tdo_value    96:*/ 0x00, 0x00, 0x00, 0x00, 0x00, 0x00, 0x00, 0x00, 
   /* tdo_value    32:*/ 0x00, 0x00, 0x00, 0x00, 
   /* Idle            */ XWAIT, Idle, Idle, 10000 // 
   /* Idle            */ XSDRTDO, // (281 bits)-DR_Select-DR_Capture-DR_Shift-DR_Update-Idle
   /* tdi_value   281:*/ 0x01, 0x20, 0xF9, 0xFF, 0xFF, 0xFF, 0xFF, 0xFF, 
   /* tdi_value   224:*/ 0xFF, 0xFF, 0xFF, 0xFF, 0xFF, 0xFF, 0xFF, 0xFF, 
   /* tdi_value   160:*/ 0xFF, 0xFF, 0xFF, 0xFF, 0xFF, 0xFF, 0xFF, 0xFF, 
   /* tdi_value    96:*/ 0xFF, 0xFF, 0xFF, 0xFF, 0xFF, 0xFF, 0xFF, 0xFF, 
   /* tdi_value    32:*/ 0xFF, 0xFF, 0xFE, 0x7C, 
   /* tdo_value   281:*/ 0x00, 0x00, 0x00, 0x00, 0x00, 0x00, 0x00, 0x00, 
   /* tdo_value   224:*/ 0x00, 0x00, 0x00, 0x00, 0x00, 0x00, 0x00, 0x00, 
   /* tdo_value   160:*/ 0x00, 0x00, 0x00, 0x00, 0x00, 0x00, 0x00, 0x00, 
   /* tdo_value    96:*/ 0x00, 0x00, 0x00, 0x00, 0x00, 0x00, 0x00, 0x00, 
   /* tdo_value    32:*/ 0x00, 0x00, 0x00, 0x00, 
   /* Idle            */ XWAIT, Idle, Idle, 10000 // 
   /* Idle            */ XSDRTDO, // (281 bits)-DR_Select-DR_Capture-DR_Shift-DR_Update-Idle
   /* tdi_value   281:*/ 0x00, 0x23, 0xC1, 0xFF, 0xFF, 0xFF, 0xFF, 0xFF, 
   /* tdi_value   224:*/ 0xFF, 0xFF, 0xFF, 0xFF, 0xFF, 0xFF, 0xFF, 0xFF, 
   /* tdi_value   160:*/ 0xFF, 0xFF, 0xFF, 0xFF, 0xFF, 0xFF, 0xFF, 0xFF, 
   /* tdi_value    96:*/ 0xFF, 0xFF, 0xFF, 0xFF, 0xFF, 0xFF, 0xFF, 0xFF, 
   /* tdi_value    32:*/ 0xFF, 0xFF, 0xFE, 0x0F, 
   /* tdo_value   281:*/ 0x00, 0x00, 0x00, 0x00, 0x00, 0x00, 0x00, 0x00, 
   /* tdo_value   224:*/ 0x00, 0x00, 0x00, 0x00, 0x00, 0x00, 0x00, 0x00, 
   /* tdo_value   160:*/ 0x00, 0x00, 0x00, 0x00, 0x00, 0x00, 0x00, 0x00, 
   /* tdo_value    96:*/ 0x00, 0x00, 0x00, 0x00, 0x00, 0x00, 0x00, 0x00, 
   /* tdo_value    32:*/ 0x00, 0x00, 0x00, 0x00, 
   /* Idle            */ XWAIT, Idle, Idle, 10000 // 
   /* Idle            */ XSDRTDO, // (281 bits)-DR_Select-DR_Capture-DR_Shift-DR_Update-Idle
   /* tdi_value   281:*/ 0x00, 0x33, 0xF9, 0xFF, 0xFF, 0xFF, 0xFF, 0xFF, 
   /* tdi_value   224:*/ 0xFF, 0xFF, 0xFF, 0xFF, 0xFF, 0xFF, 0xFF, 0xFF, 
   /* tdi_value   160:*/ 0xFF, 0xFF, 0xFF, 0xFF, 0xFF, 0xFF, 0xFF, 0xFF, 
   /* tdi_value    96:*/ 0xFF, 0xFF, 0xFF, 0xFF, 0xFF, 0xFF, 0xFF, 0xFF, 
   /* tdi_value    32:*/ 0xFF, 0xFF, 0xFE, 0x7F, 
   /* tdo_value   281:*/ 0x00, 0x00, 0x00, 0x00, 0x00, 0x00, 0x00, 0x00, 
   /* tdo_value   224:*/ 0x00, 0x00, 0x00, 0x00, 0x00, 0x00, 0x00, 0x00, 
   /* tdo_value   160:*/ 0x00, 0x00, 0x00, 0x00, 0x00, 0x00, 0x00, 0x00, 
   /* tdo_value    96:*/ 0x00, 0x00, 0x00, 0x00, 0x00, 0x00, 0x00, 0x00, 
   /* tdo_value    32:*/ 0x00, 0x00, 0x00, 0x00, 
   /* Idle            */ XWAIT, Idle, Idle, 10000 // 
   /* Idle            */ XSDRTDO, // (281 bits)-DR_Select-DR_Capture-DR_Shift-DR_Update-Idle
   /* tdi_value   281:*/ 0x01, 0x30, 0xF9, 0xFF, 0xFF, 0xFF, 0xFF, 0xFF, 
   /* tdi_value   224:*/ 0xFF, 0xFF, 0xFF, 0xFF, 0xFF, 0xFF, 0xFF, 0xFF, 
   /* tdi_value   160:*/ 0xFF, 0xFF, 0xFF, 0xFF, 0xFF, 0xFF, 0xFF, 0xFF, 
   /* tdi_value    96:*/ 0xFF, 0xFF, 0xFF, 0xFF, 0xFF, 0xFF, 0xFF, 0xFF, 
   /* tdi_value    32:*/ 0xFF, 0xFF, 0xFE, 0x7C, 
   /* tdo_value   281:*/ 0x00, 0x00, 0x00, 0x00, 0x00, 0x00, 0x00, 0x00, 
   /* tdo_value   224:*/ 0x00, 0x00, 0x00, 0x00, 0x00, 0x00, 0x00, 0x00, 
   /* tdo_value   160:*/ 0x00, 0x00, 0x00, 0x00, 0x00, 0x00, 0x00, 0x00, 
   /* tdo_value    96:*/ 0x00, 0x00, 0x00, 0x00, 0x00, 0x00, 0x00, 0x00, 
   /* tdo_value    32:*/ 0x00, 0x00, 0x00, 0x00, 
   /* Idle            */ XWAIT, Idle, Idle, 10000 // 
   /* Idle            */ XSDRTDO, // (281 bits)-DR_Select-DR_Capture-DR_Shift-DR_Update-Idle
   /* tdi_value   281:*/ 0x01, 0xB3, 0xC1, 0xFF, 0xFF, 0xFF, 0xFF, 0xFF, 
   /* tdi_value   224:*/ 0xFF, 0xFF, 0xFF, 0xFF, 0xFF, 0xFF, 0xFF, 0xFF, 
   /* tdi_value   160:*/ 0xFF, 0xFF, 0xFF, 0xFF, 0xFF, 0xFF, 0xFF, 0xFF, 
   /* tdi_value    96:*/ 0xFF, 0xFF, 0xFF, 0xFF, 0xFF, 0xFF, 0xFF, 0xFF, 
   /* tdi_value    32:*/ 0xFF, 0xFF, 0xFE, 0x0F, 
   /* tdo_value   281:*/ 0x00, 0x00, 0x00, 0x00, 0x00, 0x00, 0x00, 0x00, 
   /* tdo_value   224:*/ 0x00, 0x00, 0x00, 0x00, 0x00, 0x00, 0x00, 0x00, 
   /* tdo_value   160:*/ 0x00, 0x00, 0x00, 0x00, 0x00, 0x00, 0x00, 0x00, 
   /* tdo_value    96:*/ 0x00, 0x00, 0x00, 0x00, 0x00, 0x00, 0x00, 0x00, 
   /* tdo_value    32:*/ 0x00, 0x00, 0x00, 0x00, 
   /* Idle            */ XWAIT, Idle, Idle, 10000 // 
   /* Idle            */ XSDRTDO, // (281 bits)-DR_Select-DR_Capture-DR_Shift-DR_Update-Idle
   /* tdi_value   281:*/ 0x00, 0xB3, 0xF9, 0xFF, 0xFF, 0xFF, 0xFF, 0xFF, 
   /* tdi_value   224:*/ 0xFF, 0xFF, 0xFF, 0xFF, 0xFF, 0xFF, 0xFF, 0xFF, 
   /* tdi_value   160:*/ 0xFF, 0xFF, 0xFF, 0xFF, 0xFF, 0xFF, 0xFF, 0xFF, 
   /* tdi_value    96:*/ 0xFF, 0xFF, 0xFF, 0xFF, 0xFF, 0xFF, 0xFF, 0xFF, 
   /* tdi_value    32:*/ 0xFF, 0xFF, 0xFE, 0x7F, 
   /* tdo_value   281:*/ 0x00, 0x00, 0x00, 0x00, 0x00, 0x00, 0x00, 0x00, 
   /* tdo_value   224:*/ 0x00, 0x00, 0x00, 0x00, 0x00, 0x00, 0x00, 0x00, 
   /* tdo_value   160:*/ 0x00, 0x00, 0x00, 0x00, 0x00, 0x00, 0x00, 0x00,
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

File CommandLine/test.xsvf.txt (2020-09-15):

erase.xsv

fmoveTo(Reset)
Reset: XREPEAT(0)
Reset: XENDIR(Idle)
Reset: XENDDR(Idle)
Reset: XSTATE(Reset)
moveTo(Reset)
Reset: XSTATE(Idle)
moveTo(Idle)
Idle: XSIR(8) -> Idle
tdi_value=0000:01
moveTo(IR_Shift)
moveTo(Idle)
Idle: XSDRSIZE(32)
Idle: XTDOMASK(32)
tdo_mask=0000:0FFF8FFF
Idle: XRUNTEST(0 cycle/ms)
Idle: XSDRTDO(32) -> Idle
tdi_value=0000:00000000
tdo_value=0000:F6E5F093
moveTo(DR_Shift)
moveTo(Idle)
Idle: XSIR(8) -> Idle
tdi_value=0000:FF
moveTo(IR_Shift)
moveTo(Idle)
Idle: XSIR(8) -> Idle
tdi_value=0000:01
moveTo(IR_Shift)
moveTo(Idle)
Idle: XSDRTDO(32) -> Idle
tdi_value=0000:00000000
tdo_value=0000:F6E5F093
moveTo(DR_Shift)
moveTo(Idle)
Idle: XSIR(8) -> Idle
tdi_value=0000:FF
moveTo(IR_Shift)
moveTo(Idle)
Idle: XSIR(8) -> Idle
tdi_value=0000:01
moveTo(IR_Shift)
moveTo(Idle)
Idle: XSDRTDO(32) -> Idle
tdi_value=0000:00000000
tdo_value=0000:F6E5F093
moveTo(DR_Shift)
moveTo(Idle)
Idle: XREPEAT(0)
Idle: XREPEAT(0)
Idle: XENDIR(Idle)
Idle: XENDDR(Idle)
Idle: XSTATE(Reset)
moveTo(Reset)
Reset: XSTATE(Idle)
moveTo(Idle)
Idle: XSIR(8) -> Idle
tdi_value=0000:FF
moveTo(IR_Shift)
moveTo(Idle)
Idle: XSDRSIZE(1)
Idle: XTDOMASK(1)
tdo_mask=0000:00
Idle: XRUNTEST(0 cycle/ms)
Idle: XSDRTDO(1) -> Idle
tdi_value=0000:00
tdo_value=0000:00
moveTo(DR_Shift)
moveTo(Idle)
Idle: XSIR(8) -> Idle
tdi_value=0000:01
moveTo(IR_Shift)
moveTo(Idle)
Idle: XSDRSIZE(32)
Idle: XTDOMASK(32)
tdo_mask=0000:0FFF8FFF
Idle: XSDRTDO(32) -> Idle
tdi_value=0000:00000000
tdo_value=0000:F6E5F093
moveTo(DR_Shift)
moveTo(Idle)
Idle: XSIR(8) -> Idle
tdi_value=0000:FF
moveTo(IR_Shift)
moveTo(Idle)
Idle: XSIR(8) -> Idle
tdi_value=0000:01
moveTo(IR_Shift)
moveTo(Idle)
Idle: XSDRTDO(32) -> Idle
tdi_value=0000:00000000
tdo_value=0000:F6E5F093
moveTo(DR_Shift)
moveTo(Idle)
Idle: XSIR(8) -> Idle
tdi_value=0000:FF
moveTo(IR_Shift)
moveTo(Idle)
Idle: XSIR(8) -> Idle
tdi_value=0000:E8
moveTo(IR_Shift)
moveTo(Idle)
Idle: XENDIR(IR_Pause)
Idle: XSIR(8) -> IR_Pause
tdi_value=0000:ED
moveTo(IR_Shift)
moveTo(IR_Pause)
IR_Pause: XENDIR(Idle)
IR_Pause: XSTATE(IR_Exit2)
moveTo(IR_Exit2)
IR_Exit2: XSTATE(IR_Update)
moveTo(IR_Update)
IR_Update: XSTATE(DR_Select)
moveTo(DR_Select)
DR_Select: XSTATE(DR_Capture)
moveTo(DR_Capture)
DR_Capture: XSTATE(DR_Exit1)
moveTo(DR_Exit1)
DR_Exit1: XSTATE(DR_Pause)
moveTo(DR_Pause)
DR_Pause: XWAIT(DR_Pause, DR_Pause, 20)
moveTo(DR_Pause)
moveTo(DR_Pause)
DR_Pause: XSTATE(DR_Exit2)
moveTo(DR_Exit2)
DR_Exit2: XSTATE(DR_Update)
moveTo(DR_Update)
DR_Update: XSTATE(Idle)
moveTo(Idle)
Idle: XWAIT(Idle, Idle, 100000)
moveTo(Idle)
moveTo(Idle)
Idle: XSTATE(DR_Select)
moveTo(DR_Select)
DR_Select: XSTATE(DR_Capture)
moveTo(DR_Capture)
DR_Capture: XSTATE(DR_Exit1)
moveTo(DR_Exit1)
DR_Exit1: XSTATE(DR_Pause)
moveTo(DR_Pause)
DR_Pause: XWAIT(DR_Pause, DR_Pause, 5000)
moveTo(DR_Pause)
moveTo(DR_Pause)
DR_Pause: XWAIT(Idle, Idle, 1)
moveTo(Idle)
moveTo(Idle)
Idle: XENDIR(IR_Pause)
Idle: XSIR(8) -> IR_Pause
tdi_value=0000:F0
moveTo(IR_Shift)
moveTo(IR_Pause)
IR_Pause: XSTATE(IR_Exit2)
moveTo(IR_Exit2)
IR_Exit2: XSTATE(IR_Update)
moveTo(IR_Update)
IR_Update: XSTATE(Idle)
moveTo(Idle)
Idle: XWAIT(Idle, Idle, 20)
moveTo(Idle)
moveTo(Idle)
Idle: XENDIR(IR_Pause)
Idle: XSIR(8) -> IR_Pause
tdi_value=0000:F0
moveTo(IR_Shift)
moveTo(IR_Pause)
IR_Pause: XSTATE(IR_Exit2)
moveTo(IR_Exit2)
IR_Exit2: XSTATE(IR_Update)
moveTo(IR_Update)
IR_Update: XSTATE(DR_Select)
moveTo(DR_Select)
DR_Select: XSTATE(DR_Capture)
moveTo(DR_Capture)
DR_Capture: XSTATE(DR_Exit1)
moveTo(DR_Exit1)
DR_Exit1: XSTATE(DR_Update)
moveTo(DR_Update)
DR_Update: XSTATE(Idle)
moveTo(Idle)
Idle: XWAIT(Idle, Idle, 800)
moveTo(Idle)
moveTo(Idle)
Idle: XENDIR(Idle)
Idle: XSIR(8) -> Idle
tdi_value=0000:C0
moveTo(IR_Shift)
moveTo(Idle)
Idle: XWAIT(Idle, Idle, 100)
moveTo(Idle)
moveTo(Idle)
Idle: XSIR(8) -> Idle
tdi_value=0000:C0
moveTo(IR_Shift)
moveTo(Idle)
Idle: XWAIT(Idle, Idle, 100)
moveTo(Idle)
moveTo(Idle)
Idle: XSIR(8) -> Idle
tdi_value=0000:E8
moveTo(IR_Shift)
moveTo(Idle)
Idle: XENDIR(IR_Pause)
Idle: XSIR(8) -> IR_Pause
tdi_value=0000:EA
moveTo(IR_Shift)
moveTo(IR_Pause)
IR_Pause: XSDRSIZE(281)
IR_Pause: XTDOMASK(281)
tdo_mask=0000:0000000000000000000000000000000000000000000000000000000000000000
tdo_mask=0100:00000000
IR_Pause: XSDRTDO(281) -> Idle
tdi_value=0000:0003C1FFFFFFFFFFFFFFFFFFFFFFFFFFFFFFFFFFFFFFFFFFFFFFFFFFFFFFFFFF
tdi_value=0100:FFFFFE0F
tdo_value=0000:0000000000000000000000000000000000000000000000000000000000000000
tdo_value=0100:00000000
moveTo(DR_Shift)
moveTo(Idle)
Idle: XENDIR(Idle)
Idle: XWAIT(Idle, Idle, 10000)
moveTo(Idle)
moveTo(Idle)
Idle: XSDRTDO(281) -> Idle
tdi_value=0000:0103F9FFFFFFFFFFFFFFFFFFFF7FFFFFFFBBFEFFFFFFFFFFFFFFFFFFFFFFFFFF
tdi_value=0100:FFFFFE7F
tdo_value=0000:0000000000000000000000000000000000000000000000000000000000000000
tdo_value=0100:00000000
moveTo(DR_Shift)
moveTo(Idle)
Idle: XWAIT(Idle, Idle, 10000)
moveTo(Idle)
moveTo(Idle)
Idle: XSDRTDO(281) -> Idle
tdi_value=0000:0180F9FFFFFFFFFFFFFFFFFFFFFFFFFFFFFFFFFFFFFFFFFFFFFFFFFFFFFFFFFF
tdi_value=0100:FFFFFE7C
tdo_value=0000:0000000000000000000000000000000000000000000000000000000000000000
tdo_value=0100:00000000
moveTo(DR_Shift)
moveTo(Idle)
Idle: XWAIT(Idle, Idle, 10000)
moveTo(Idle)
moveTo(Idle)
Idle: XSDRTDO(281) -> Idle
tdi_value=0000:0083C1FFFFFFFFFFFFFFFFFFFFFFFFFFFFFFFFFFFFFFFFFFFFFFFFFFFFFFFFFF
tdi_value=0100:FFFFFE0F
tdo_value=0000:0000000000000000000000000000000000000000000000000000000000000000
tdo_value=0100:00000000
moveTo(DR_Shift)
moveTo(Idle)
Idle: XWAIT(Idle, Idle, 10000)
moveTo(Idle)
moveTo(Idle)
Idle: XSDRTDO(281) -> Idle
tdi_value=0000:00C3F9FFFFFFFFFFFFFFFFFFFFFFFFFFFFFFFFFFFFFFFFFFFFFFFFFFFFFFFFFF
tdi_value=0100:FFFFFE7F
tdo_value=0000:0000000000000000000000000000000000000000000000000000000000000000
tdo_value=0100:00000000
moveTo(DR_Shift)
moveTo(Idle)
Idle: XWAIT(Idle, Idle, 10000)
moveTo(Idle)
moveTo(Idle)
Idle: XSDRTDO(281) -> Idle
tdi_value=0000:01C0F9FFFFFFFFFFFFFFFFFFFFFFFFFFFFFFFFFFFFFFFFFFFFFFFFFFFFFFFFFF
tdi_value=0100:FFFFFE7C
tdo_value=0000:0000000000000000000000000000000000000000000000000000000000000000
tdo_value=0100:00000000
moveTo(DR_Shift)
moveTo(Idle)
Idle: XWAIT(Idle, Idle, 10000)
moveTo(Idle)
moveTo(Idle)
Idle: XSDRTDO(281) -> Idle
tdi_value=0000:0143C1FFFFFFFFFFFFFFFFFFFFFFFFFFFFFFFFFFFFFFFFFFFFFFFFFFFFFFFFFF
tdi_value=0100:FFFFFE0F
tdo_value=0000:0000000000000000000000000000000000000000000000000000000000000000
tdo_value=0100:00000000
moveTo(DR_Shift)
moveTo(Idle)
Idle: XWAIT(Idle, Idle, 10000)
moveTo(Idle)
moveTo(Idle)
Idle: XSDRTDO(281) -> Idle
tdi_value=0000:0043F9FFFFFFFFFFFFFFFFFFFFFFFFFFFFFFFFFFFFFFFFFFFFFFFFFFFFFFFFFF
tdi_value=0100:FFFFFE7F
tdo_value=0000:0000000000000000000000000000000000000000000000000000000000000000
tdo_value=0100:00000000
moveTo(DR_Shift)
moveTo(Idle)
Idle: XWAIT(Idle, Idle, 10000)
moveTo(Idle)
moveTo(Idle)
Idle: XSDRTDO(281) -> Idle
tdi_value=0000:0060F9FFFFFFFFFFFFFFFFFFFFFFFFFFFFFFFFFFFFFFFFFFFFFFFFFFFFFFFFFF
tdi_value=0100:FFFFFE7C
tdo_value=0000:0000000000000000000000000000000000000000000000000000000000000000
tdo_value=0100:00000000
moveTo(DR_Shift)
moveTo(Idle)
Idle: XWAIT(Idle, Idle, 10000)
moveTo(Idle)
moveTo(Idle)
Idle: XSDRTDO(281) -> Idle
tdi_value=0000:0163C1FFFFFFFFFFFFFFFFFFFFFFFFFFFFFFFFFFFFFFFFFFFFFFFFFFFFFFFFFF
tdi_value=0100:FFFFFE0F
tdo_value=0000:0000000000000000000000000000000000000000000000000000000000000000
tdo_value=0100:00000000
moveTo(DR_Shift)
moveTo(Idle)
Idle: XWAIT(Idle, Idle, 10000)
moveTo(Idle)
moveTo(Idle)
Idle: XSDRTDO(281) -> Idle
tdi_value=0000:01E3F9FFFFFFFFFFFFFFFFFFFFFFFFFFFFFFFFFFFFFFFFFFFFFFFFFFFFFFFFFF
tdi_value=0100:FFFFFE7F
tdo_value=0000:0000000000000000000000000000000000000000000000000000000000000000
tdo_value=0100:00000000
moveTo(DR_Shift)
moveTo(Idle)
Idle: XWAIT(Idle, Idle, 10000)
moveTo(Idle)
moveTo(Idle)
Idle: XSDRTDO(281) -> Idle
tdi_value=0000:00E0F9FFFFFFFFFFFFFFFFFFFFFFFFFFFFFFFFFFFFFFFFFFFFFFFFFFFFFFFFFF
tdi_value=0100:FFFFFE7C
tdo_value=0000:0000000000000000000000000000000000000000000000000000000000000000
tdo_value=0100:00000000
moveTo(DR_Shift)
moveTo(Idle)
Idle: XWAIT(Idle, Idle, 10000)
moveTo(Idle)
moveTo(Idle)
Idle: XSDRTDO(281) -> Idle
tdi_value=0000:00A3C1FFFFFFFFFFFFFFFFFFFFFFFFFFFFFFFFFFFFFFFFFFFFFFFFFFFFFFFFFF
tdi_value=0100:FFFFFE0F
tdo_value=0000:0000000000000000000000000000000000000000000000000000000000000000
tdo_value=0100:00000000
moveTo(DR_Shift)
moveTo(Idle)
Idle: XWAIT(Idle, Idle, 10000)
moveTo(Idle)
moveTo(Idle)
Idle: XSDRTDO(281) -> Idle
tdi_value=0000:01A3F9FFFFFFFFFFFFFFFFFFFFFFFFFFFFFFFFFFFFFFFFFFFFFFFFFFFFFFFFFF
tdi_value=0100:FFFFFE7F
tdo_value=0000:0000000000000000000000000000000000000000000000000000000000000000
tdo_value=0100:00000000
moveTo(DR_Shift)
moveTo(Idle)
Idle: XWAIT(Idle, Idle, 10000)
moveTo(Idle)
moveTo(Idle)
Idle: XSDRTDO(281) -> Idle
tdi_value=0000:0120F9FFFFFFFFFFFFFFFFFFFFFFFFFFFFFFFFFFFFFFFFFFFFFFFFFFFFFFFFFF
tdi_value=0100:FFFFFE7C
tdo_value=0000:0000000000000000000000000000000000000000000000000000000000000000
tdo_value=0100:00000000
moveTo(DR_Shift)
moveTo(Idle)
Idle: XWAIT(Idle, Idle, 10000)
moveTo(Idle)
moveTo(Idle)
Idle: XSDRTDO(281) -> Idle
tdi_value=0000:0023C1FFFFFFFFFFFFFFFFFFFFFFFFFFFFFFFFFFFFFFFFFFFFFFFFFFFFFFFFFF
tdi_value=0100:FFFFFE0F
tdo_value=0000:0000000000000000000000000000000000000000000000000000000000000000
tdo_value=0100:00000000
moveTo(DR_Shift)
moveTo(Idle)
Idle: XWAIT(Idle, Idle, 10000)
moveTo(Idle)
moveTo(Idle)
Idle: XSDRTDO(281) -> Idle
tdi_value=0000:0033F9FFFFFFFFFFFFFFFFFFFFFFFFFFFFFFFFFFFFFFFFFFFFFFFFFFFFFFFFFF
tdi_value=0100:FFFFFE7F
tdo_value=0000:0000000000000000000000000000000000000000000000000000000000000000
tdo_value=0100:00000000
moveTo(DR_Shift)
moveTo(Idle)
Idle: XWAIT(Idle, Idle, 10000)
moveTo(Idle)
moveTo(Idle)
Idle: XSDRTDO(281) -> Idle
tdi_value=0000:0130F9FFFFFFFFFFFFFFFFFFFFFFFFFFFFFFFFFFFFFFFFFFFFFFFFFFFFFFFFFF
tdi_value=0100:FFFFFE7C
tdo_value=0000:0000000000000000000000000000000000000000000000000000000000000000
tdo_value=0100:00000000
moveTo(DR_Shift)
moveTo(Idle)
Idle: XWAIT(Idle, Idle, 10000)
moveTo(Idle)
moveTo(Idle)
Idle: XSDRTDO(281) -> Idle
tdi_value=0000:01B3C1FFFFFFFFFFFFFFFFFFFFFFFFFFFFFFFFFFFFFFFFFFFFFFFFFFFFFFFFFF
tdi_value=0100:FFFFFE0F
tdo_value=0000:0000000000000000000000000000000000000000000000000000000000000000
tdo_value=0100:00000000
moveTo(DR_Shift)
moveTo(Idle)
Idle: XWAIT(Idle, Idle, 10000)
moveTo(Idle)
moveTo(Idle)
Idle: XSDRTDO(281) -> Idle
tdi_value=0000:00B3F9FFFFFFFFFFFFFFFFFFFFFFFFFFFFFFFFFFFFFFFFFFFFFFFFFFFFFFFFFF
tdi_value=0100:FFFFFE7F
tdo_value=0000:0000000000000000000000000000000000000000000000000000000000000000
tdo_value=0100:00000000
moveTo(DR_Shift)
moveTo(Idle)
Idle: XWAIT(Idle, Idle, 10000)
moveTo(Idle)
moveTo(Idle)
Idle: XSDRTDO(281) -> Idle
tdi_value=0000:00F0F9FFFFFFFFFFFFFFFFFFFFFFFFFFFFFFFFFFFFFFFFFFFFFFFFFFFFFFFFFF
tdi_value=0100:FFFFFE7C
tdo_value=0000:0000000000000000000000000000000000000000000000000000000000000000
tdo_value=0100:00000000
moveTo(DR_Shift)
moveTo(Idle)
Idle: XWAIT(Idle, Idle, 10000)
moveTo(Idle)
moveTo(Idle)
Idle: XSDRTDO(281) -> Idle
tdi_value=0000:01F3C1FFFFFFFFFFFFFFFFFFFFFFFFFFFFFFFFFFFFFFFFFFFFFFFFFFFFFFFFFF
tdi_value=0100:FFFFFE0F
tdo_value=0000:0000000000000000000000000000000000000000000000000000000000000000
tdo_value=0100:00000000
moveTo(DR_Shift)
moveTo(Idle)
Idle: XWAIT(Idle, Idle, 10000)
moveTo(Idle)
moveTo(Idle)
Idle: XSDRTDO(281) -> Idle
tdi_value=0000:0173F9FFFFFFFFFFFFFFFFFFFFFFFFFFFFFFFFFFFFFFFFFFFFFFFFFFFFFFFFFF
tdi_value=0100:FFFFFE7F
tdo_value=0000:0000000000000000000000000000000000000000000000000000000000000000
tdo_value=0100:00000000
moveTo(DR_Shift)
moveTo(Idle)
Idle: XWAIT(Idle, Idle, 10000)
moveTo(Idle)
moveTo(Idle)
Idle: XSDRTDO(281) -> Idle
tdi_value=0000:0070F9FFFFFFFFFFFFFFFFFFFFFFFFFFFFFFE187FFFFFFFFFFFFFFFFFFFFFFFF
tdi_value=0100:FFFFFE7C
tdo_value=0000:0000000000000000000000000000000000000000000000000000000000000000
tdo_value=0100:00000000
moveTo(DR_Shift)
moveTo(Idle)
Idle: XWAIT(Idle, Idle, 10000)
moveTo(Idle)
moveTo(Idle)
Idle: XSDRTDO(281) -> Idle
tdi_value=0000:0053C1FFFFFFFFFFFFFFFFFFFFFFFFFFFFFFFFFFFFFFFFFFFFFFFFFFFFFFFFFF
tdi_value=0100:FFFFFE0F
tdo_value=0000:0000000000000000000000000000000000000000000000000000000000000000
tdo_value=0100:00000000
moveTo(DR_Shift)
moveTo(Idle)
Idle: XWAIT(Idle, Idle, 10000)
moveTo(Idle)
moveTo(Idle)
Idle: XSDRTDO(281) -> Idle
tdi_value=0000:0153F9FFFFFFFFFFFFFFFFFFFFFFFFFFFFFFFFFFFFFFFFFFFFFFFFFFFFFFFFFF
tdi_value=0100:FFFFFE7F
tdo_value=0000:0000000000000000000000000000000000000000000000000000000000000000
tdo_value=0100:00000000
moveTo(DR_Shift)
moveTo(Idle)
Idle: XWAIT(Idle, Idle, 10000)
moveTo(Idle)
moveTo(Idle)
Idle: XSDRTDO(281) -> Idle
tdi_value=0000:01D0F9FFFFFFFFFFFFFFFFFFFFFFFFFFFFFFFFFFFFFFFFFFFFFFFFFFFFFFFFFF
tdi_value=0100:FFFFFE7C
tdo_value=0000:0000000000000000000000000000000000000000000000000000000000000000
tdo_value=0100:00000000
moveTo(DR_Shift)
moveTo(Idle)
Idle: XWAIT(Idle, Idle, 10000)
moveTo(Idle)
moveTo(Idle)
Idle: XSDRTDO(281) -> Idle
tdi_value=0000:00D3C1FFFFFFFFFFFFFFFFFFFFFFFFFFFFFFFFFFFFFFFFFFFFFFFFFFFFFFFFFF
tdi_value=0100:FFFFFE0F
tdo_value=0000:0000000000000000000000000000000000000000000000000000000000000000
tdo_value=0100:00000000
moveTo(DR_Shift)
moveTo(Idle)
Idle: XWAIT(Idle, Idle, 10000)
moveTo(Idle)
moveTo(Idle)
Idle: XSDRTDO(281) -> Idle
tdi_value=0000:0093F9FFFFFFFFFFFFFFFFFFFFFFFFFFFFFFFFFFFFFFFFFFFFFFFFFFFFFFFFFF
tdi_value=0100:FFFFFE7F
tdo_value=0000:0000000000000000000000000000000000000000000000000000000000000000
tdo_value=0100:00000000
moveTo(DR_Shift)
moveTo(Idle)
Idle: XWAIT(Idle, Idle, 10000)
moveTo(Idle)
moveTo(Idle)
Idle: XSDRTDO(281) -> Idle
tdi_value=0000:0190F9FFFFFFFFFFFFFFFFFFFFFFFFFFFFFFFFFFFFFFFFFFFFFFFFFFFFFFFFFF
tdi_value=0100:FFFFFE7C
tdo_value=0000:0000000000000000000000000000000000000000000000000000000000000000
tdo_value=0100:00000000
moveTo(DR_Shift)
moveTo(Idle)
Idle: XWAIT(Idle, Idle, 10000)
moveTo(Idle)
moveTo(Idle)
Idle: XSDRTDO(281) -> Idle
tdi_value=0000:0113C1FFFFFFFFFFFFFFFFFFFFFFFFFFFFFFFFFFFFFFFFFFFFFFFFFFFFFFFFFF
tdi_value=0100:FFFFFE0F
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

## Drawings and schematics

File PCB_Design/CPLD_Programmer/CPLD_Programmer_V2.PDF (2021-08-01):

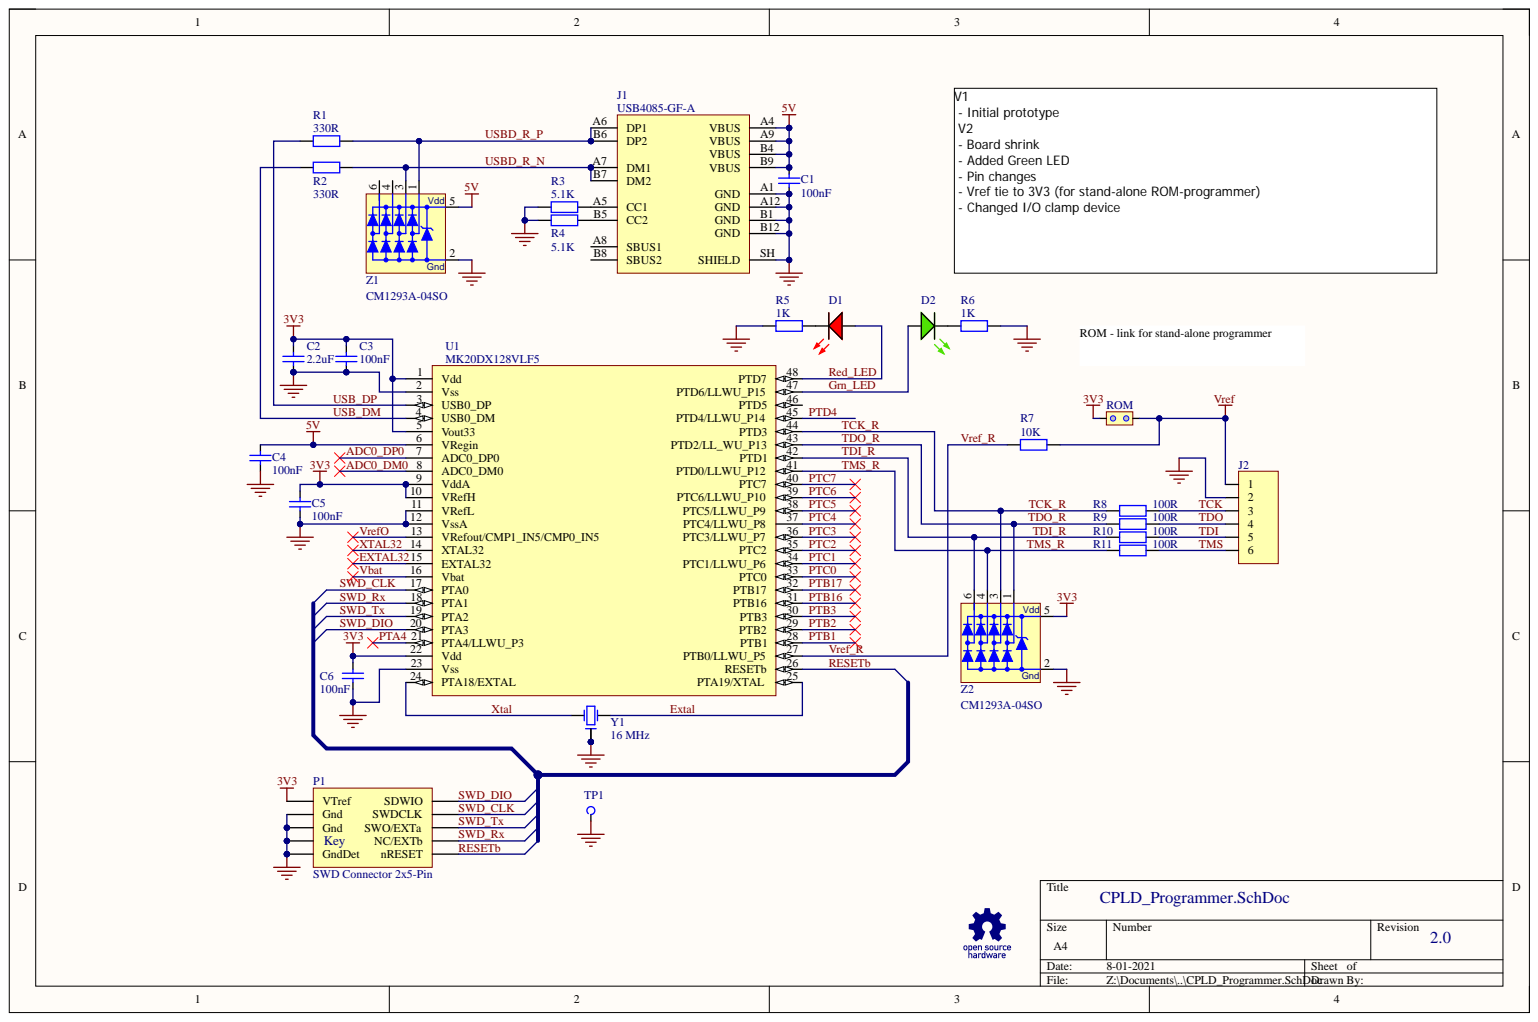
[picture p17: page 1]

- Initial prototype
- Board shrink
- Added Green LED
- Pin changes
- Vref tie to 3V3 (for stand-alone ROM-programmer)
- Changed I/O clamp device

ROM - link for stand-alone programmer

ADC0_DP0 7 | TDI_R
ADC0_DM0 8 | TMS_R

100nF | VssA 12 | PTC4 | TDO_R R9 | | 100R TDO

VrefO | VRefout/CMP1_IN5/CMP0_IN5 13 | PTC3 | TDI_R R10 | | 100R TDI

XTAL32 14 | PTC2 | TMS_R R11 | | 100R TMS

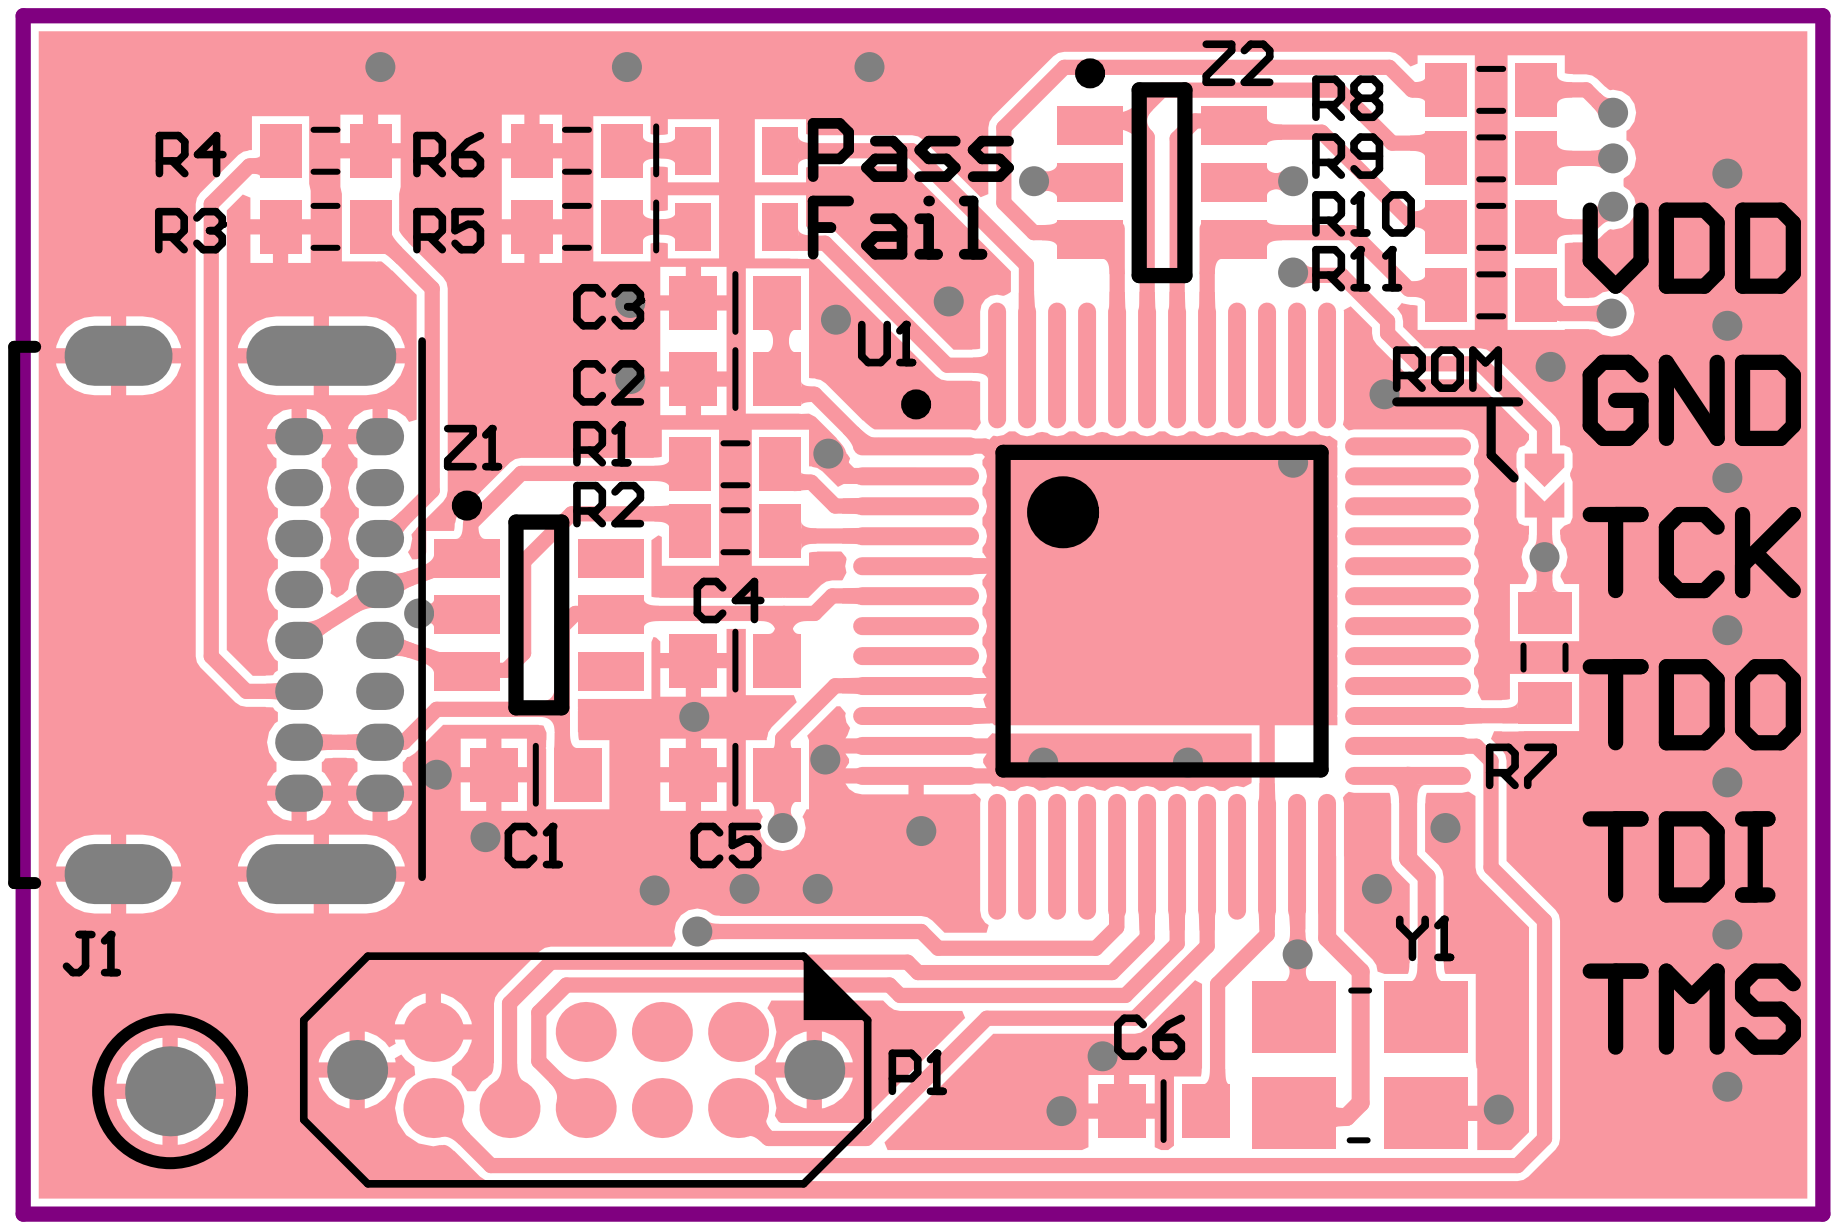
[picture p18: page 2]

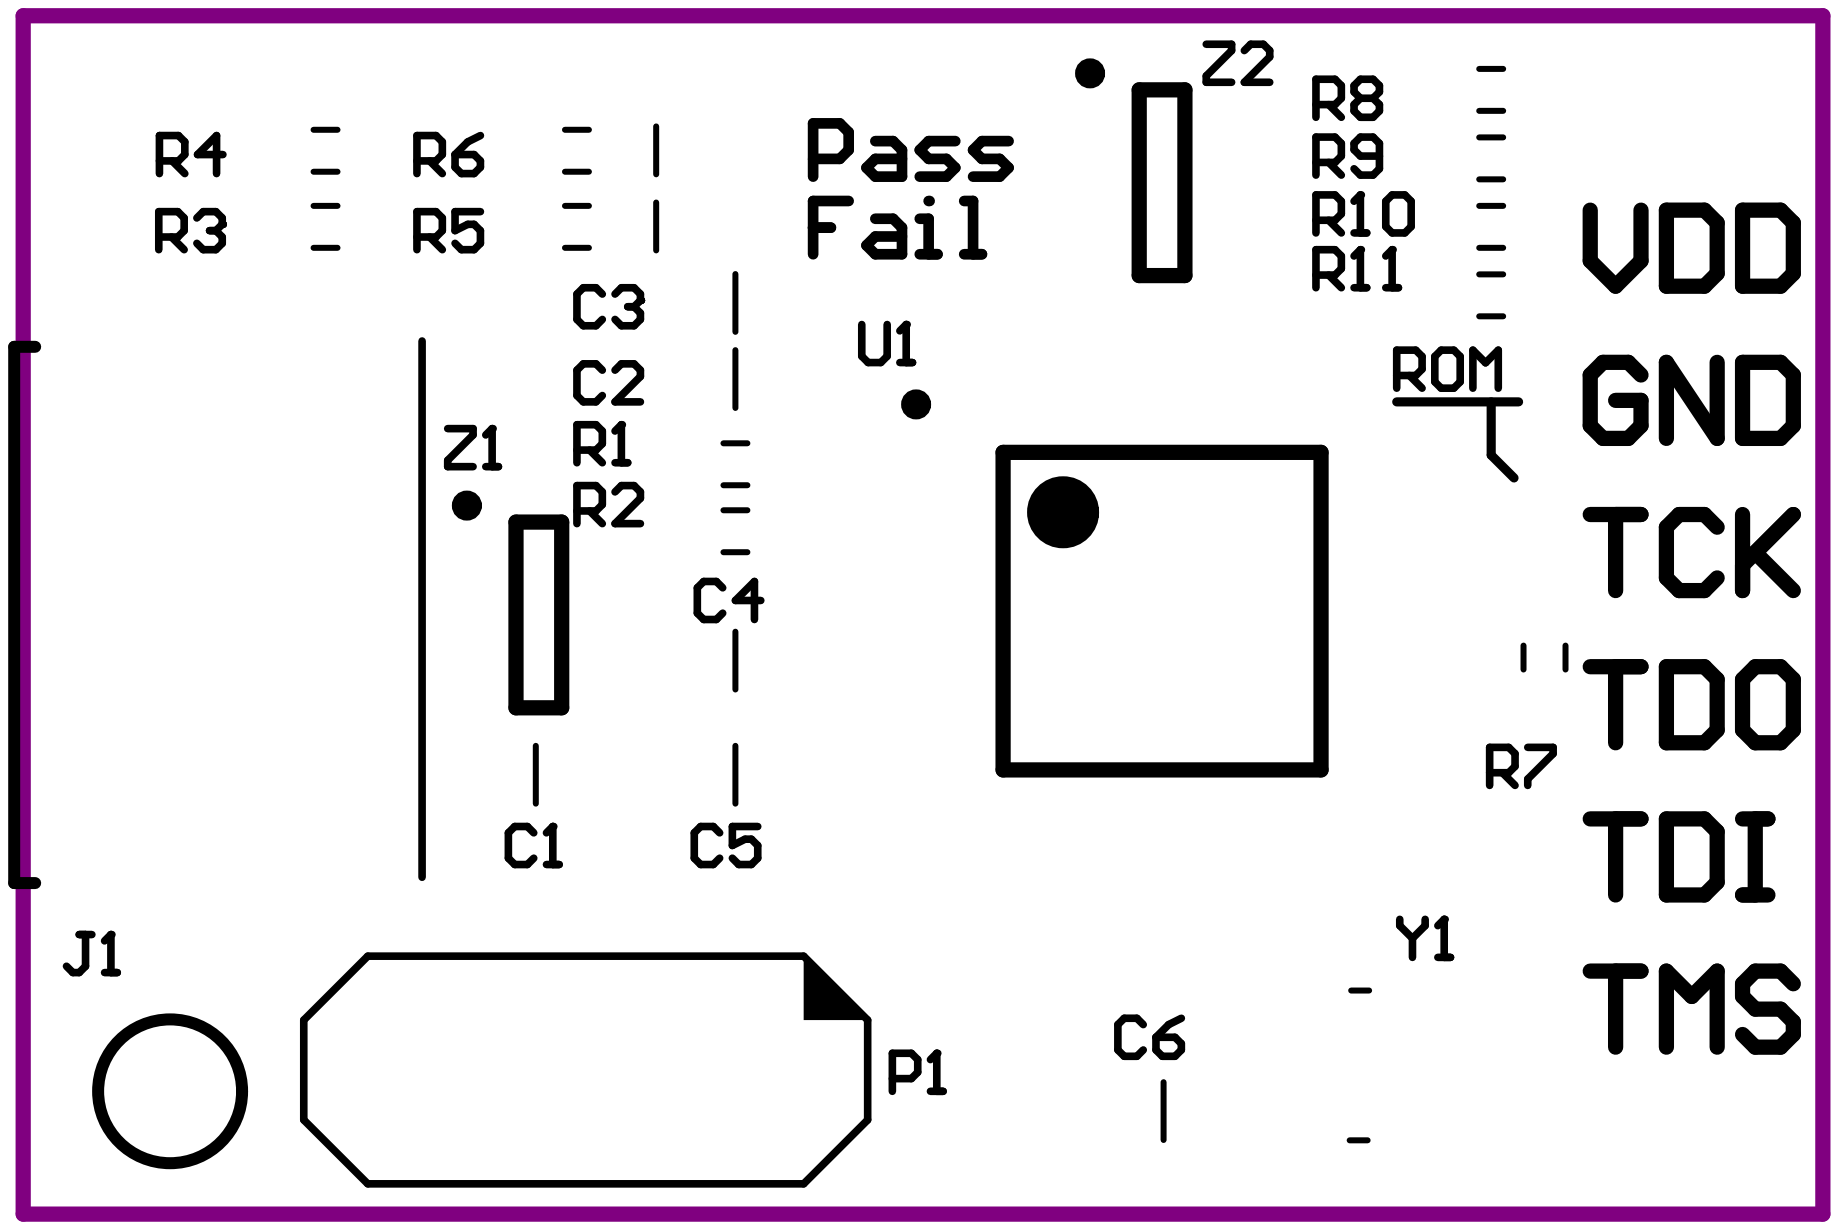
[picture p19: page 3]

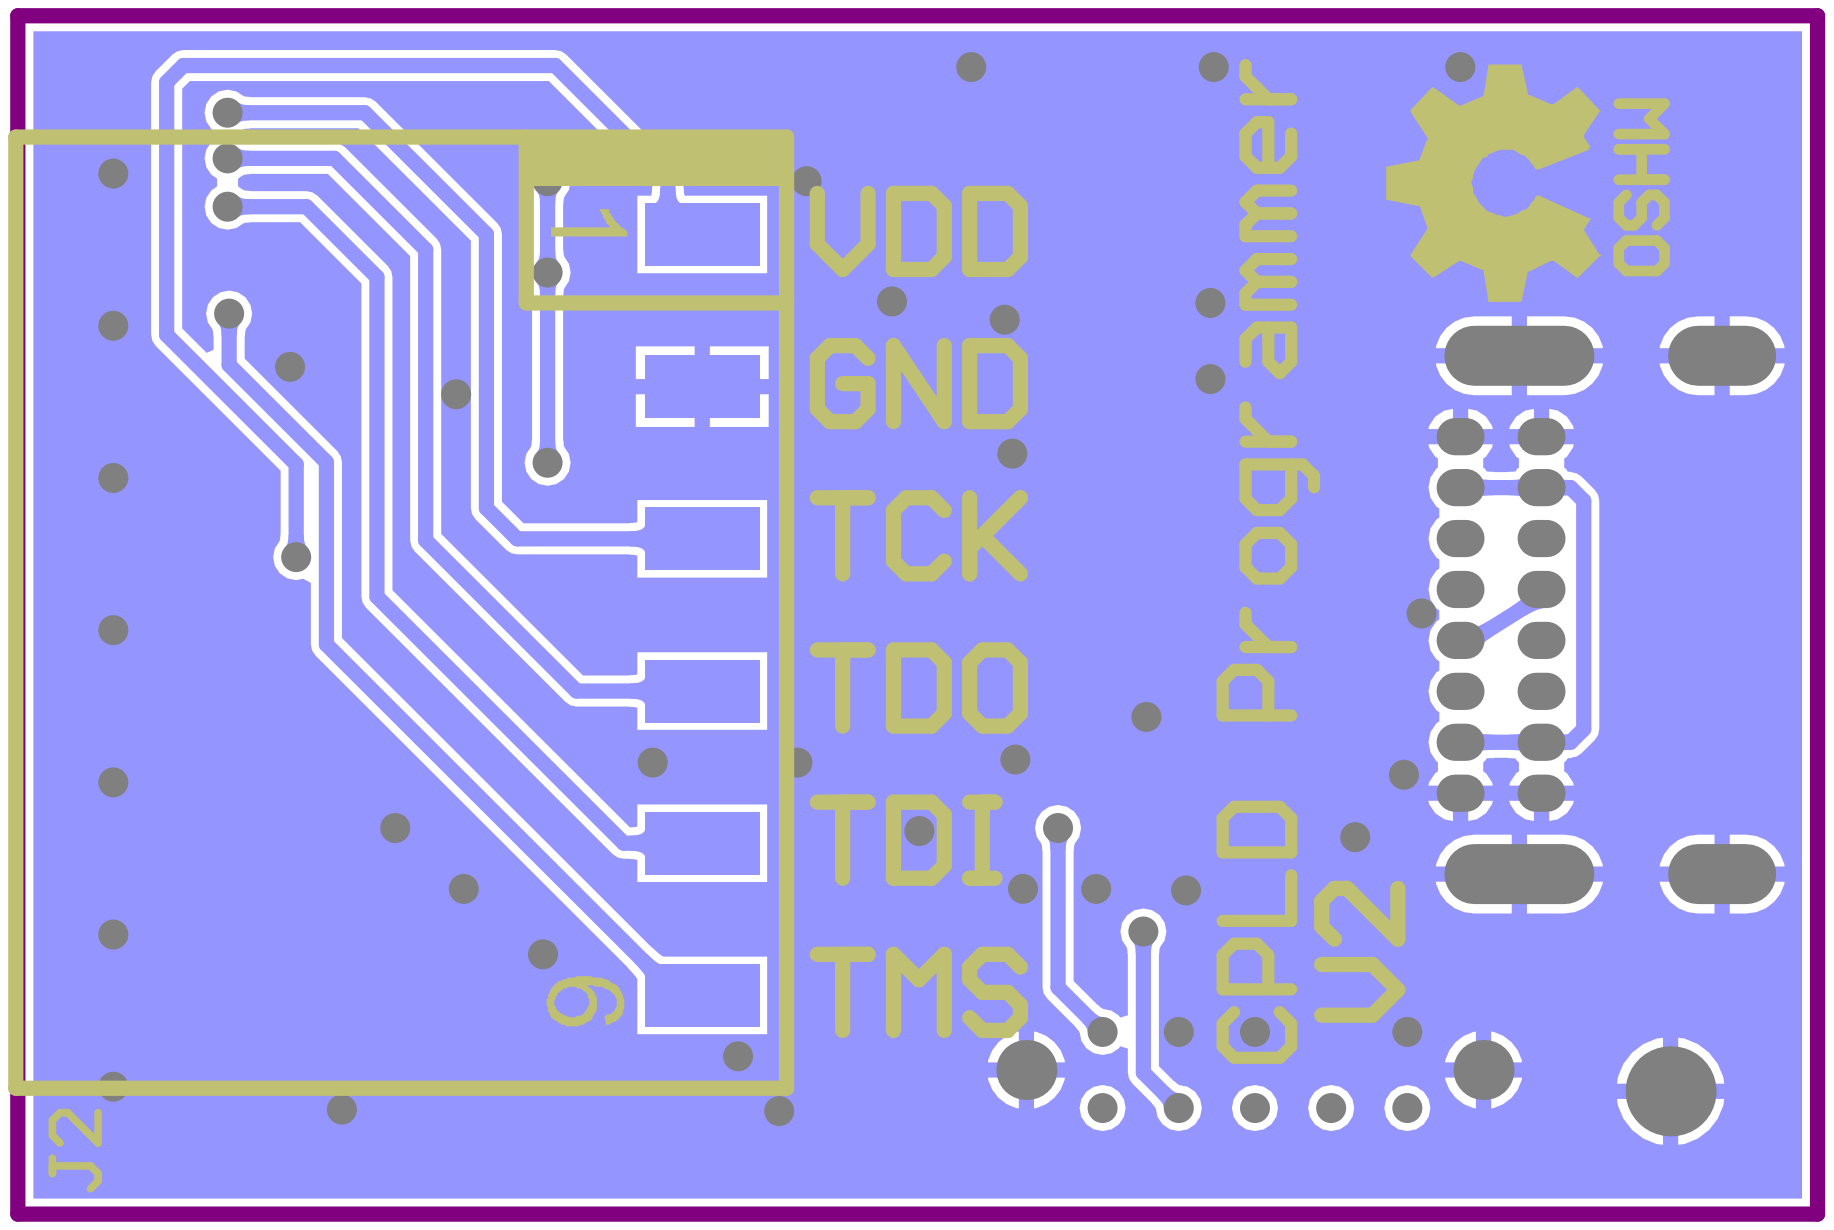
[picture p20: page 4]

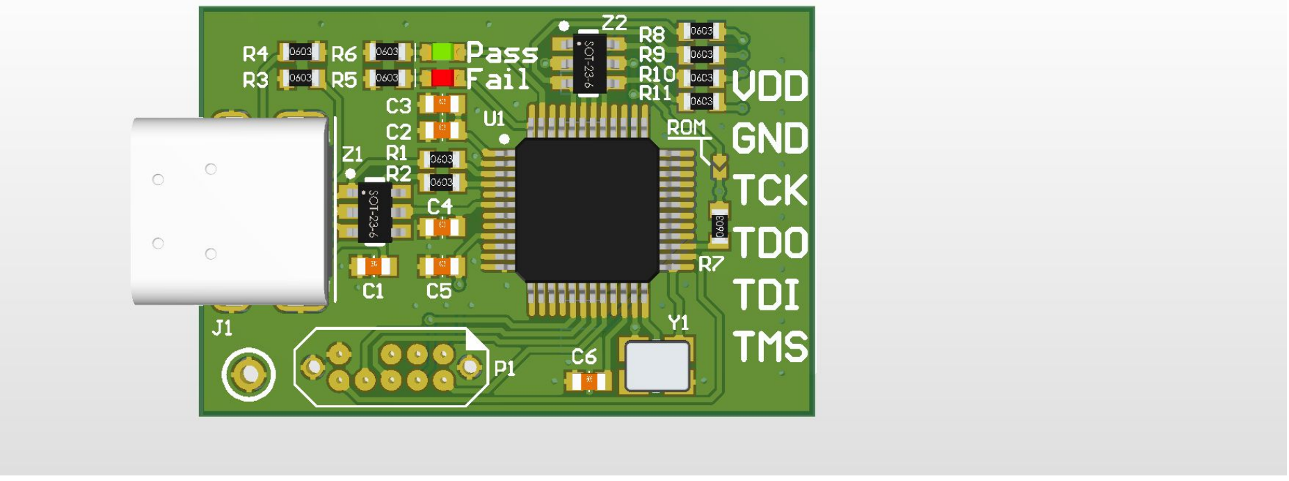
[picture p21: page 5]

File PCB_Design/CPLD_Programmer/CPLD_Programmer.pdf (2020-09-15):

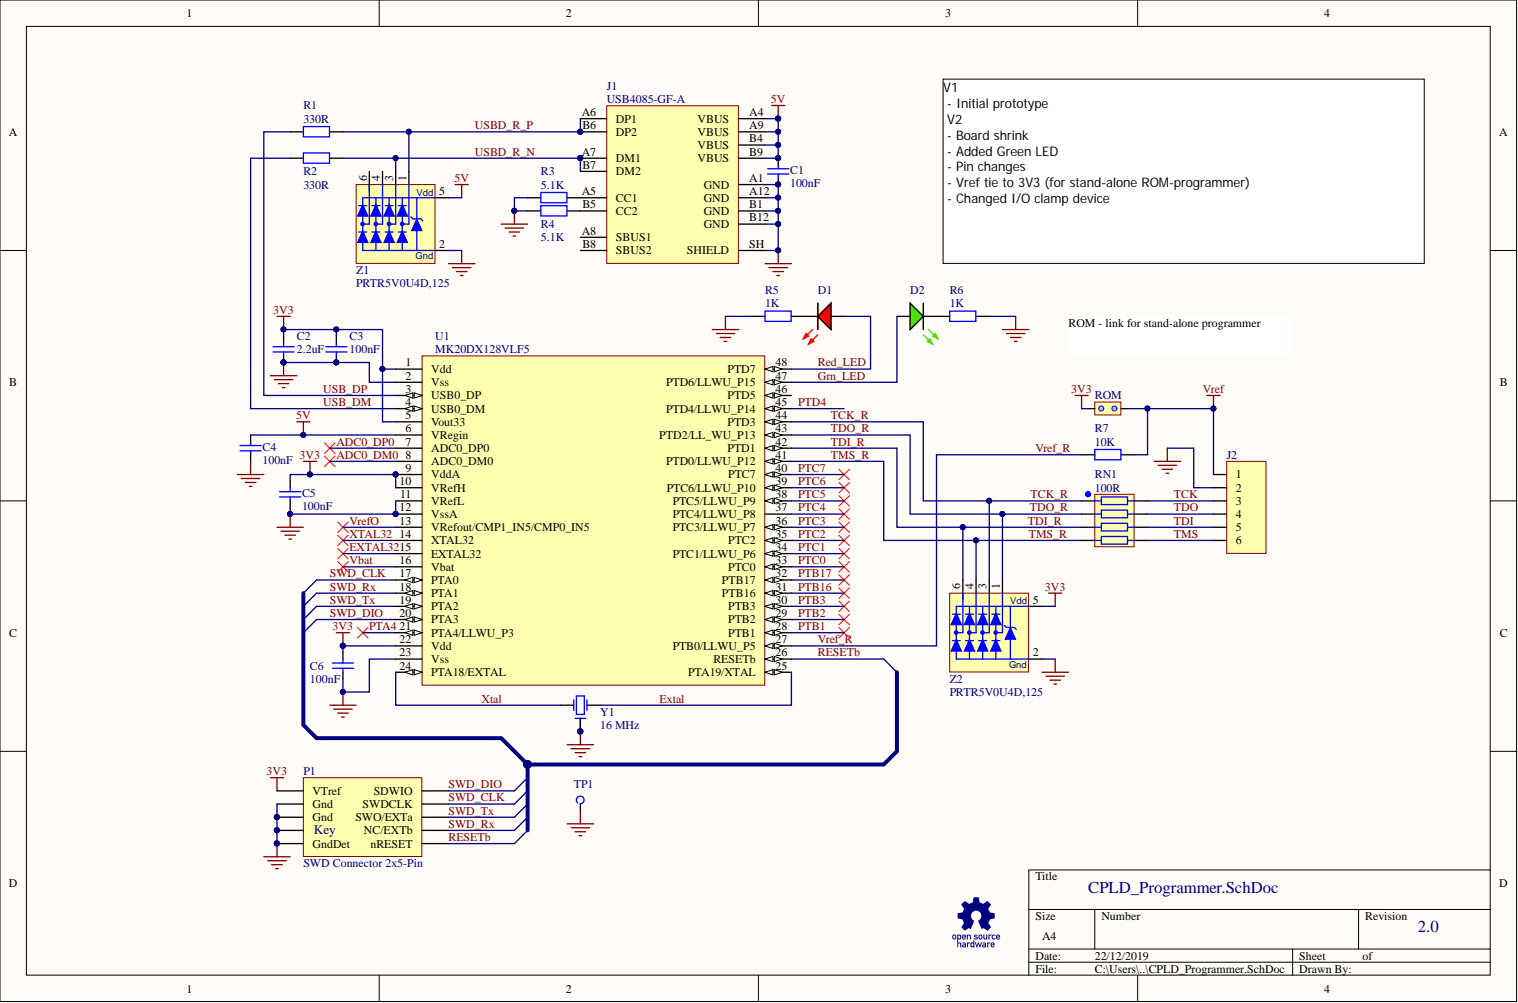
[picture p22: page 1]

- Initial prototype
- Board shrink
- Added Green LED
- Pin changes
- Vref tie to 3V3 (for stand-alone ROM-programmer)
- Changed I/O clamp device

ROM - link for stand-alone programmer

Vout33 5
VRegin 6 | TDO_R
ADC0_DP0 7 | TDI_R
ADC0_DM0 8 | Vref_R TMS_R

100nF | | VssA 12 | | PTC4 | TDO_R | | TDO

VrefO | VRefout/CMP1_IN5/CMP0_IN5 13 | | PTC3 | | TDI_R | | TDI

XTAL32 14 | | PTC2 | | | TMS_R | | TMS
EXTAL32 15 | | | | | | 3V3

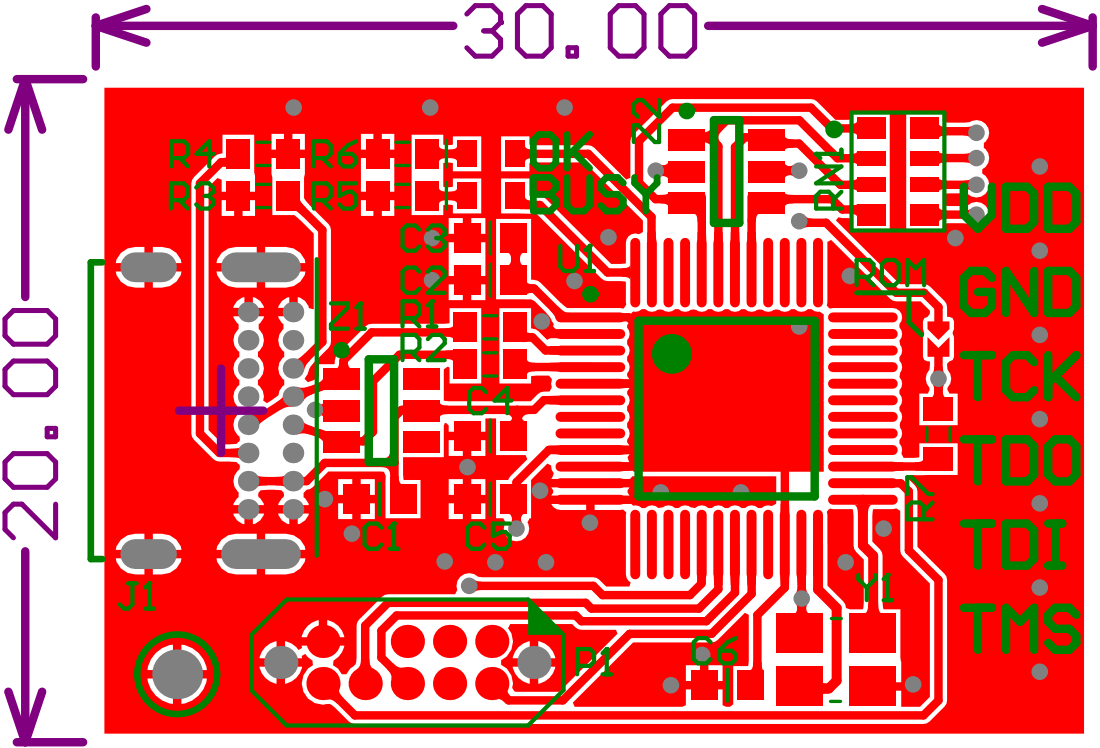
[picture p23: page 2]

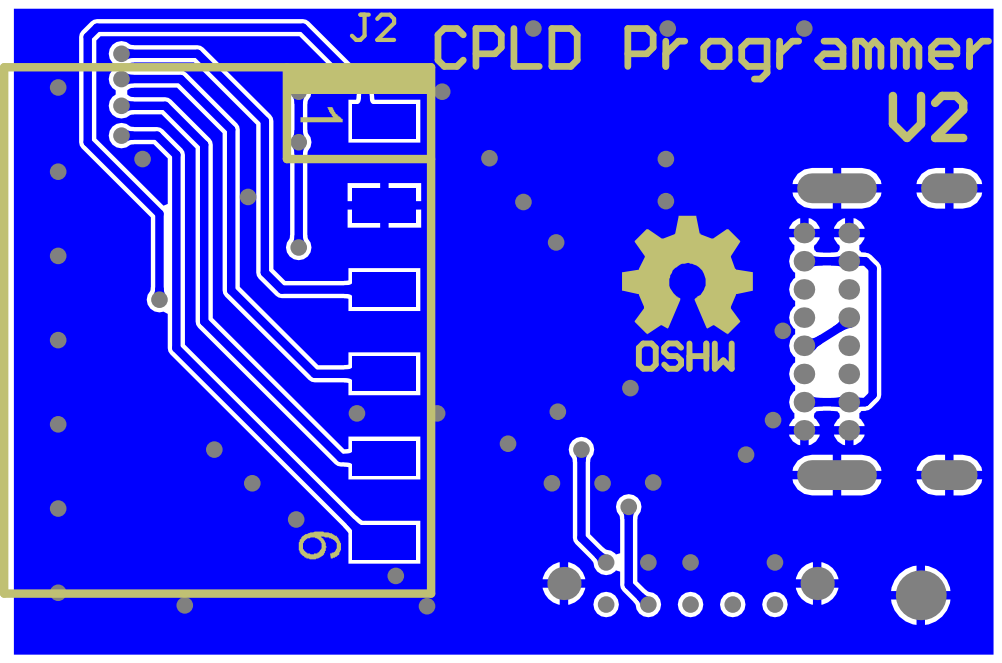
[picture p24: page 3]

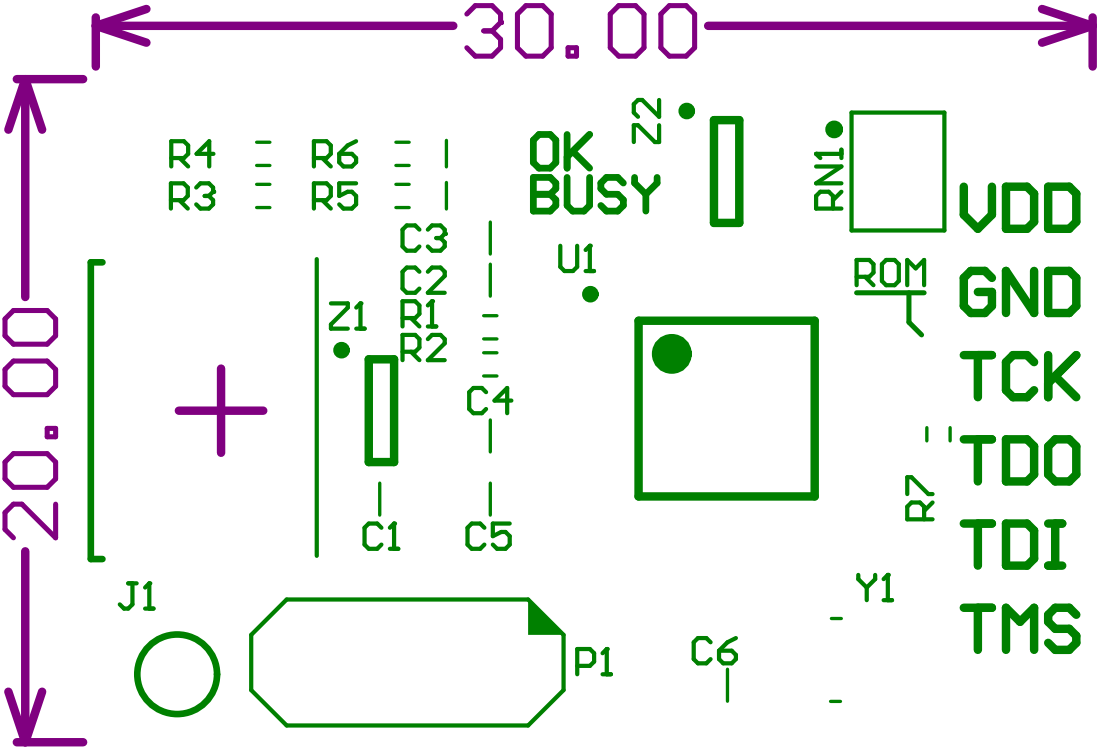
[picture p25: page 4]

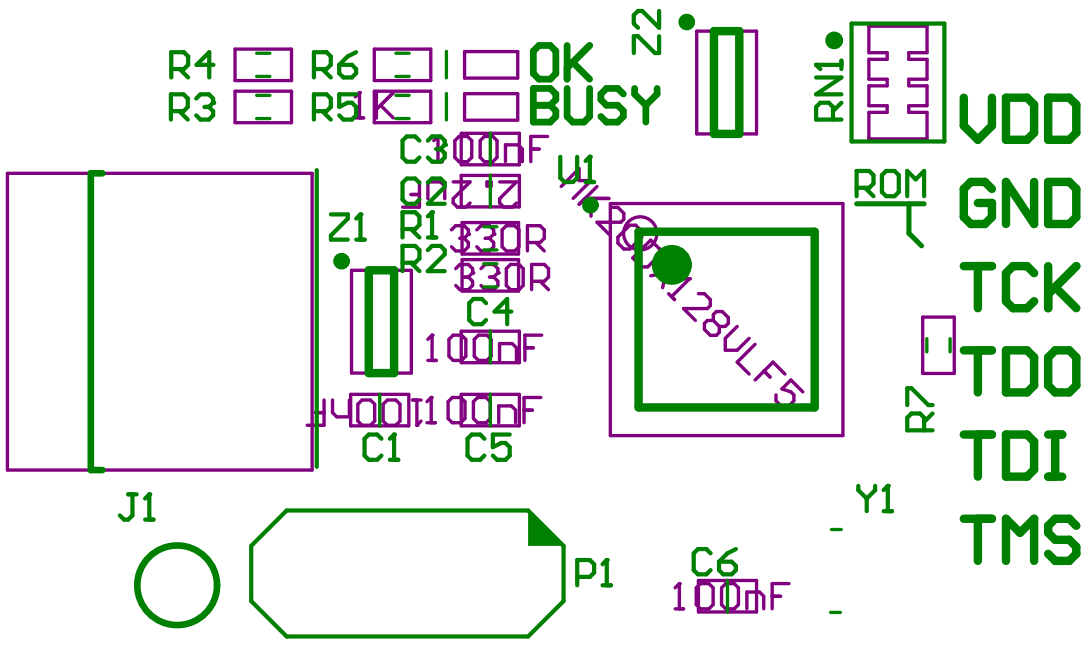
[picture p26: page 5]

Bill of Materials | Bill of Materials for Project [CPLD_Programmer.PrjPcb] (No PCB Document Selected)
Source Data From: | | CPLD_Programmer.PrjPcb
Project: | | CPLD_Programmer.PrjPcb
Variant: | | None
Creation Date: | 22/12/2019 | 12:39 PM
Print Date: | 22-Dec-19 | 12:39:24 PM
Footprint | Comment | FarnellPN | Digikey | LCSC | Designator | Description | Quantity
CCNP1608-0603_N | 100nF | | | C14663 | C1, C3, C4, C5, C6 | Capacitor non-polar SMT 0603 | 5
CCNP1608-0603_N | 2.2uF | | | C23630 | C2 | Capacitor non-polar SMT 0603 | 1
LED1608-0603-RED_N | LED Red | 1581239 | | C2286 | D1 | LED 0603 Red | 1
LED1608-0603-GREEN_N | LED Green | 1581242 | | C72043 | D2 | LED 0603 Green | 1
USB4085-GF-A | USB4085-GF-A | 2924867 | 2073-USB4085-GF-ACT-
SAMTEC-SMH-106-02-X-S | Header, 6-Pin | 2084265 (sim) | SAM15786-ND | | J2 | Header, 6-Pin | 1
CR1608-0603_N | 330R | | | C22775 | R1, R2 | Resistor SMT 0603 | 2

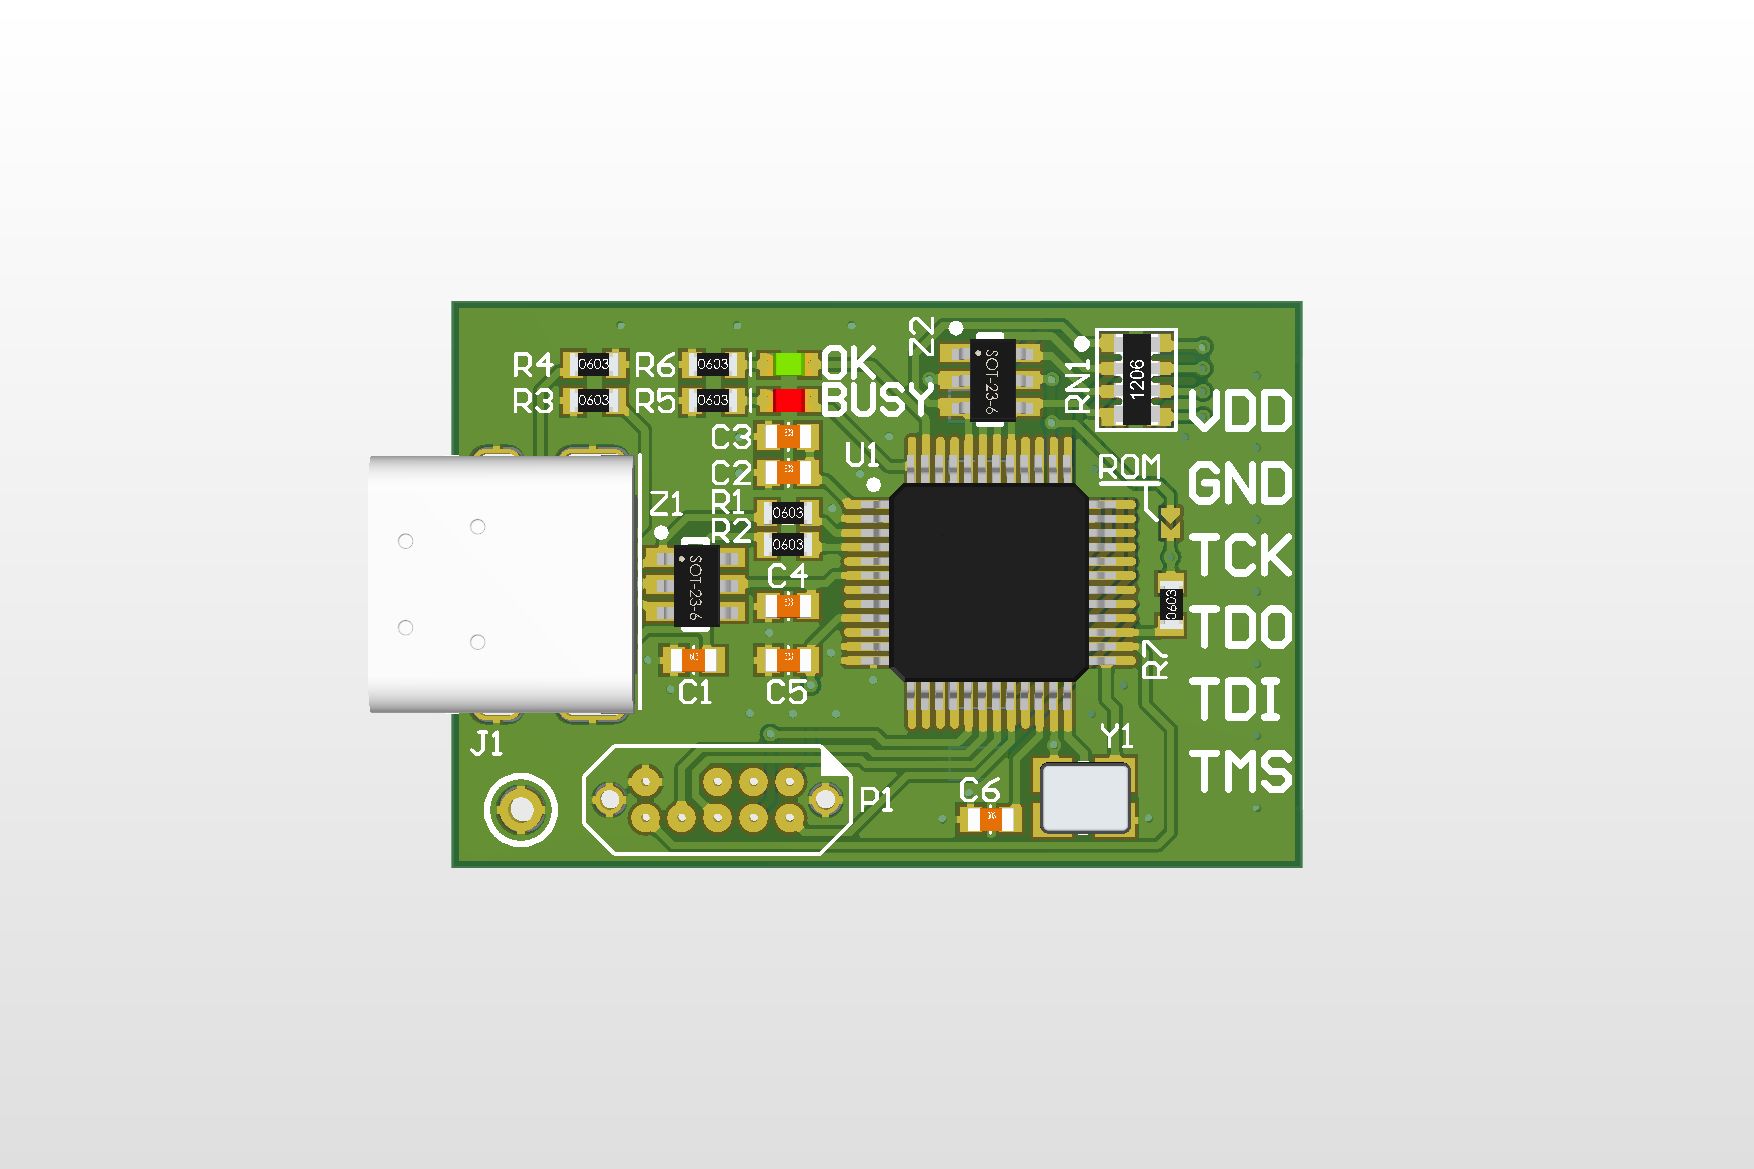
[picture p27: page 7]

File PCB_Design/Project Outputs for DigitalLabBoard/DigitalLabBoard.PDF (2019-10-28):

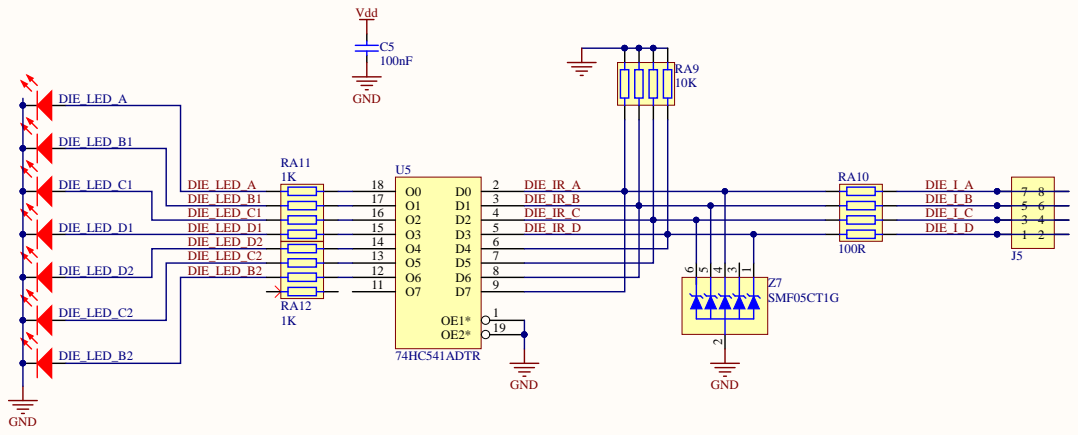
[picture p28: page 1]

DIE_LED_C1 | | 1 | O6 12 O5 13 O4 14 O3 15 O2 16 O1 17 O0 18 | 4 | DIE_IR_C

3 | DIE_IR_B

DIE_LED_C2 | 7


O4 14 | LED_IR3
O3 15 | LED_IR4

LED_D4 | O2 16 | LED_IR5

O1 17 | LED_IR6
O0 18 | LED_IR7

LED_D5


USBDP | USB0_DP 3 | PTD5
USBDM | USB0_DM 4 | PTD4



PB_OR3
PB_OR4 | | PB_O3

15 16
13 14 1 10 11 12 2 3 4 5 6 7 8 9


EW_PED_O | | 3 4
NS_CAR_O | 5 6

EW_LIGHTS1_I | 9 10
EW_LIGHTS0_I | | 11 12
NS_LIGHTS1_I | | | 13 14

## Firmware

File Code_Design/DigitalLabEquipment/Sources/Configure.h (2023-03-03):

/*
 * Configure.h
 *
 *  This file defines how the microcontroller pins and peripherals are being used.
 *
 *  Created on: 30 Oct 2019
 *      Author: podonoghue
 */

#ifndef SOURCES_CONFIGURE_H_
#define SOURCES_CONFIGURE_H_

#include "hardware.h"
#include "i2c.h"

/// Interval x5ms for switch debouncing/unlatching
static constexpr unsigned DEBOUNCE_INTERVAL_COUNT = 20/5;

/// Interval x5ms for switch latching
static constexpr unsigned LATCHED_INTERVAL_COUNT = 2000/5;

/// Interval x5ms for switch initial auto-repeat for frequency
static constexpr unsigned AUTO_REPEAT_COUNT = 1000/5;

/// Interval x5ms for switch auto-repeat for frequency
static constexpr unsigned AUTO_REPEAT_RATE = 500/5;

/// Interval x5ms for power switch delay
static constexpr unsigned POWER_BUTTON_DELAY_COUNT = 200/5;

/// Interval x5ms for power-up delay before power checks start (ADC)
static constexpr unsigned POWER_ON_ADC_DELAY_COUNT = 20/5;

/// Interval x5ms for power-up delay before notifying peripherals
static constexpr unsigned POWER_ON_DELAY_COUNT = 100/5;

/*
 * TRAFFIC SIMULATOR
 */
/// I2C address for Traffic intersection GPIO expander
/// IO0_7-0 = Fixed direction user I/O
/// IO1_7-0 = Outputs to LEDs (active high)
static constexpr uint8_t TRAFFIC_I2C_ADDRESS = 0b001;

/**
 * Extract north-south lights from user input
 *
 * @param portValue Port value from IO0_7-0
 *
 * @return 0-3 indicating light encoding
 */
static constexpr inline unsigned northSouthLights(unsigned portValue) {
   // Traffic intersection - Mask for north-south LIGHTS input from user (GPIO expander outputs IO0_1-0)
   constexpr uint8_t NS_LIGHTS_IN_OFFSET      = 0;
   constexpr uint8_t NS_LIGHTS_IN_MASK        = 0b11U<<NS_LIGHTS_IN_OFFSET;

   return (portValue & NS_LIGHTS_IN_MASK)>>NS_LIGHTS_IN_OFFSET;
}

/**
 * Extract east-west lights from user input
 *
 * @param portValue Port value from IO0_7-0
 *
 * @return 0-3 indicating light encoding
 */
static constexpr inline unsigned eastWestLights(unsigned portValue) {
   // Traffic intersection - Masks for LIGHTS input from user (GPIO expander outputs IO0_3-2)
   constexpr uint8_t EW_LIGHTS_IN_OFFSET      = 2;
   constexpr uint8_t EW_LIGHTS_IN_MASK        = 0b11U<<(EW_LIGHTS_IN_OFFSET);

   return (portValue & EW_LIGHTS_IN_MASK)>>EW_LIGHTS_IN_OFFSET;
}

/**
 * Encode north-south and east-west light values to LED mask
 *
 * @param nsLights   North-south lights input
 * @param ewLights   East-west lights input
 */
static constexpr inline unsigned trafficLedsEncode(unsigned nsLights, unsigned ewLights) {
   /// Traffic intersection - Mask for LEDs (GPIO expander outputs IO1_(3..0)/IO1_(7..4))
   enum {
      RED_LED_MASK         = 0b0001,
      AMBER_LED_MASK       = 0b0010,
      GREEN_LED_MASK       = 0b0100,
      PEDESTRIAN_LED_MASK  = 0b1000,
   };

   // Encoding for traffic LEDs
   const uint8_t lightTable[] = {
         RED_LED_MASK,                          // Red
         AMBER_LED_MASK,                        // Amber
         GREEN_LED_MASK,                        // Green
         GREEN_LED_MASK|PEDESTRIAN_LED_MASK,    // Green + Walk
   };

   // Offsets for LEDs (GPIO expander outputs IO1_(7..4)/IO1_(3..0))
   constexpr unsigned EW_LED_OFFSET = 0;
   constexpr unsigned NS_LED_OFFSET = 4;

   return (lightTable[nsLights]<<NS_LED_OFFSET)|(lightTable[ewLights]<<EW_LED_OFFSET);
}

/// I2C address for debounced buttons GPIO expander
/// IO0_7-0 = Outputs to user
/// IO1_7-0 = Inputs from switches/Outputs to LEDs (active-low)
static constexpr uint8_t BUTTON_I2C_ADDRESS  = 0b000;

#endif /* SOURCES_CONFIGURE_H_ */

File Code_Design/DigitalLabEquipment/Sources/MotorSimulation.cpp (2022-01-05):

/*
 * MotorSImulation.cpp
 *
 *  Created on: 30 Oct 2019
 *      Author: podonoghue
 */

#include "MotorSimulation.h"
#include "Configure.h"

using namespace USBDM;

/**
 * Data for 1 Charlieplexed LED
 */
struct CharlieData {
   uint8_t highPin;
   uint8_t lowPin;
};

/**
 * Data for Charlieplexed LEDs
 * In clockwise sequence
 */
static const CharlieData charlieData[] = {
      // High    Low
      // 3210    3210
      {0b0000, 0b0000}, // Off

      {0b0001, 0b1000}, // Physical LED #12
      {0b1000, 0b0001}, // Physical LED #11
      {0b0010, 0b1000}, // Physical LED #10
      {0b1000, 0b0010}, // Physical LED #9
      {0b0001, 0b0100}, // Physical LED #8
      {0b0100, 0b0001}, // Physical LED #7
      {0b0100, 0b1000}, // Physical LED #6
      {0b1000, 0b0100}, // Physical LED #5
      {0b0010, 0b0100}, // Physical LED #4
      {0b0100, 0b0010}, // Physical LED #3
      {0b0001, 0b0010}, // Physical LED #2
      {0b0010, 0b0001}, // Physical LED #1
};

/**
 * Turn on given LED
 *
 * @param ledNum
 */
void MotorSimulator::writeLed(unsigned ledNum) {
   CharliePlexing::write(charlieData[ledNum].highPin);
   CharliePlexing::setDirection(charlieData[ledNum].highPin|charlieData[ledNum].lowPin);
}

/**
 * Motor phases
 */
enum Phase {
   Phase0 = 0b00,
   Phase1 = 0b01,
   Phase2 = 0b10,
   Phase3 = 0b11,
};

/**
 * Called when an illegal motor input sequence has been detected
 */
void MotorSimulator::motorAbort() {
}

/**
 * FTM call-back
 * Polls motor inputs and implements a simple state-machine
 *
 * Sequence
 *
 *         Expected Input
 * Phase   Hold   CW     CCW
 *   0:    0b1000 0b0010 0b0001
 *   1:    0b0010 0b0100 0b1000
 *   2:    0b0100 0b0001 0b0010
 *   3:    0b0001 0b1000 0b0100
 */
void MotorSimulator::timerCallback() {

   static uint8_t  lastInput = 0;

   if (!powerOn) {
      return;
   }

   uint8_t input = MotorPhases::read();

   // Wait until input is stable for 1 sample period
   if (input != lastInput) {
      lastInput = input;
      return;
   }

   // Enable on 1st user input
   enabled = enabled || (input != 0b0000);

   if (!enabled) {
      return;
   }

   Phase phase = (Phase)(motorPosition&0b11);

   switch (phase) {
      default:
      case Phase0:
         if (input == 0b1000) {
            // No action
         }
         else if (input == 0b0010) {
            motorPosition++;
         }
         else if (input == 0b0001) {
            motorPosition--;
         }
         else {
            motorAbort();
         }
         break;
      case Phase1:
         if (input == 0b0010) {
            // No action
         }
         else if (input == 0b0100) {
            motorPosition++;
         }
         else if (input == 0b1000) {
            motorPosition--;
         }
         else {
            motorAbort();
         }
         break;
      case Phase2:
         if (input == 0b0100) {
            // No action
         }
         else if (input == 0b0001) {
            motorPosition++;
         }
         else if (input == 0b0010) {
            motorPosition--;
         }
         else {
            motorAbort();
         }
         break;
      case Phase3:
         if (input == 0b0001) {
            // No action
         }
         else if (input == 0b1000) {
            motorPosition++;
         }
         else if (input == 0b0100) {
            motorPosition--;
         }
         else {
            motorAbort();
         }
         break;
   }
   if (motorPosition == 0) {
      motorPosition = 12;
   }
   if (motorPosition > 12) {
      motorPosition = 1;
   }
   // Update display
   writeLed(motorPosition);
}

/**
 * Test motor LEDs
 */
void MotorSimulator::testMotorLeds() {
   CharliePlexing::setInOut(
         PinPull_None,
         PinDriveStrength_High,
         PinDriveMode_PushPull,
         PinAction_None,
         PinFilter_None,
         PinSlewRate_Slow);

   motorPosition++;
   if (motorPosition>12) {
      motorPosition = 1;
   }
   writeLed(motorPosition);
}

/**
 * Notification that soft power-on has occurred
 */
void MotorSimulator::softPowerOn() {

   CharliePlexing::setInOut(
         PinPull_None,
         PinDriveStrength_High,
         PinDriveMode_PushPull,
         PinAction_None,
         PinFilter_None,
         PinSlewRate_Slow);

   MotorPhases::setInput(
         PinPull_None,
         PinAction_None,
         PinFilter_None);

   auto cb = []() {
      This->timerCallback();
   };

   writeLed(enabled?motorPosition:LEDS_OFF);

   powerOn = true;

   MotorPitChannel::setCallback(cb);
   MotorPitChannel::enableNvicInterrupts(NvicPriority_Normal);
   MotorPitChannel::configure(1_ms, PitChannelIrq_Enabled);
}

/**
 * Notification that soft power-off is about to occur
 */
void MotorSimulator::softPowerOff() {

   powerOn = false;

   MotorPitChannel::configure(1_ms, PitChannelIrq_Disabled);

   writeLed(LEDS_OFF);
}

/// Self pointer for static methods e.g. call-backs
MotorSimulator *MotorSimulator::This = nullptr;

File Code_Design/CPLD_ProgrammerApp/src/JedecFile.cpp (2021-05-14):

/** ============================================================================
 * JedecFile.cpp
 *
 *  Created on: 29 Dec 2019
 *      Author: podonoghue
 *  ============================================================================ */
#include <cctype>
#include <cstring>

#include "JedecFile.h"
#include "DeviceMapFile.h"

using namespace std;

/**
 * Read JEDEC file
 *
 * @param jedec_filepath FILE to read
 *
 * @return nullptr    => success
 * @return != nullptr => error message
 */
const char *JedecFile::loadFile(const char *jedec_filepath) {
   FILE *fp = fopen(jedec_filepath, "rb");
   if (fp == nullptr) {
      return "Failed to open file";
   }
   const char *msg = loadFile(fp);
   fclose(fp);

   if (msg != nullptr) {
      return msg;
   }
   if (calculateChecksum() != check_sum) {
      msg = "Invalid checksum";
   }
   return msg;
}

/**
 * Read JEDEC file from fp
 *
 * @param fp FILE to read
 *
 * @return nullptr    => success
 * @return != nullptr => error message
 */
const char *JedecFile::loadFile(FILE *fp) {
   char     comment[1000];
   char     *comment_ptr   = comment;
   unsigned fuse_number    = 0;

   State state       = S_HEADER;
   bool stripSpace   = true;

   auto saveCharacter = [&comment_ptr, &comment](char ch) {
      if (comment_ptr<(comment+sizeof(comment)-1)) {
         *comment_ptr++ = ch;
         *comment_ptr   = '\0'; // Keep '\0' terminated for debug
      }
   };

   auto resetBuffer = [&comment_ptr, &comment]() {
      comment_ptr = comment;
   };

   auto stripTrailing = [&comment_ptr]() {
      do {
         *comment_ptr-- = '\0';
      } while (isspace(*comment_ptr));
   };

   int ch;
   do {
      ch = fgetc(fp);
      //fprintf(stderr,  "%c", (char)ch); fflush(stderr);
      if ((ch == ETX) || (ch == -1)) {
         break;
      }
      if ((ch =='\r') || (ch == '\n')) {
         continue;
      }
      switch (state) {
         case S_HEADER:
            if (ch == STX) {
               state = S_COMMAND;
            }
            continue;
            break;
         case S_COMMAND:
         {
            switch(ch) {
               case 'N':
                  state          = S_COMMENT;
                  resetBuffer();
                  saveCharacter('N');
                  stripSpace     = false;
                  break;
               case 'Q':   state = S_QCOMMAND;      break;
               case 'F':   state = S_FUSEDEFAULT;   break;
               case 'X':   state = S_X;             break;
               case 'J':   state = S_J_arch;        break;
               case 'C':   state = S_CHECKSUM;      break;
               case 'L':
                  state = S_L_num;
                  fuse_number = 0;
                  break;
               default:
                  return "Unexpected command character";
            }
            continue;
         }
         case S_CHECKSUM:
            if (ch == '*') {
               state = S_COMMAND;
               continue;
            }
            if ((ch>='0')&&(ch<='9')) {
               check_sum = 16*check_sum + (ch-'0');
               continue;
            }
            if ((ch>='a')&&(ch<='f')) {
               check_sum = 16*check_sum + (ch-'a') + 10;
               continue;
            }
            if ((ch>='A')&&(ch<='F')) {
               check_sum = 16*check_sum + (ch-'A') + 10;
               continue;
            }
            else {
               return "Expected digit";
            }
            break;
         case S_COMMENT:
            if (ch == '*') {
               state = S_COMMAND;
               // Strip trailing spaces
               stripTrailing();
               //printf("Note: \'%s\'\n", comment);
               continue;
            }
            // Strip leading spaces
            if (isspace(ch) && stripSpace) {
               continue;
            }
            stripSpace = false;
            saveCharacter(ch);
            if (strncmp(comment,"N ",2) == 0) {
               // Strip 'Note' from front on special note lines
               resetBuffer();
               stripSpace  = true;
            }
            if (strncmp(comment,"Note ",5) == 0) {
               // Strip 'Note' from front on special note lines
               resetBuffer();
               stripSpace  = true;
            }
            if (strncmp(comment,"DEVICE",6) == 0) {
               resetBuffer();
               stripSpace  = true;
               state = S_COMMENT_device;
            }
            if (strncmp(comment,"VERSION",7) == 0) {
               resetBuffer();
               stripSpace  = true;
               state = S_COMMENT_version;
            }
            continue;
         case S_COMMENT_version:
            if (ch == '*') {
               state = S_COMMAND;
               saveCharacter('\0');
               version_info = strdup(comment);
               //printf("Version: \'%s\'\n", comment);
               continue;
            }
            if (isspace(ch) && stripSpace) {
               continue;
            }
            stripSpace = false;
            saveCharacter(ch);
            continue;
         case S_COMMENT_device:
            if (ch == '*') {
               state = S_COMMAND;
               saveCharacter('\0');
               device_name = strdup(comment);
               //printf("Device: \'%s\'\n", comment);
               continue;
            }
            if (isspace(ch) && stripSpace) {
               continue;
            }
            stripSpace = false;
            saveCharacter(ch);
            continue;
         case S_QCOMMAND:
         {
            switch(ch) {
               case 'F': state = S_QF;    break;
               case 'P': state = S_QP;    break;
               case 'V': state = S_QV;    break;
               default:  return "Unexpected character in Q..";
            }
            continue;
         }
         case S_QF:
            if (isdigit(ch)) {
               fuse_limit = 10*fuse_limit+(ch-'0');
               continue;
            }
            if (ch == '*') {
               fuse_data.allocateFuses(fuse_limit);
               //printf("fuse_limit = %d\n", fuse_limit);
               state = S_COMMAND;
               continue;
            }
            return "Expected digit";
         case S_QP:
            if (ch == '*') {
               state = S_COMMAND;
               //printf("number_of_pins = %d\n", number_of_pins);
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

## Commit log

2019-10-26 Still Innitial design
    [DigitalLabBoard_Die.SchDoc, DigitalLabBoard_LEDs.SchDoc, DigitalLabBoard_Processor.SchDoc, DigitalLabBoard_Stepper.SchDoc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]
2019-10-28 Still Initial design work
    [DigitalLabBoard_LEDs.SchDoc, DigitalLabBoard_Processor.SchDoc, DigitalLabBoard_Switches.SchDoc, DigitalLabBoard_Traffic.SchDoc]
2019-11-05 Checked DRCs and changed fonts
    [Bill of Materials-DigitalLabBoard.xls, DigitalLabBoard.GBL, DigitalLabBoard.GBO, DigitalLabBoard.GTL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]
2019-11-06 Reduced board length by 5 mm and moved USB-C Connector to fit in box better. Fixed orientation of some components to agree with JLCPCB production
    [BOM - Edited.xls, Bill of Materials-DigitalLabBoard.xls, Bill of Materials-DigitalLabBoardX.xls, DigitalLabBoard.GBL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]
2019-11-07 First Design spin
    [BOM - Edited.xls, Bill of Materials-DigitalLabBoard.xls, DigitalLabBoard.GBL, DigitalLabBoard.GBO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]
2019-11-11 Added JLC PCB serial number location
    [BOM - Edited.xls, Bill of Materials-DigitalLabBoard.xls, DigitalLabBoard.GBL, DigitalLabBoard.GBO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]
2019-11-14 Review of PC after first spin. - Added power monitor - Moved breadboard power posts - change traffic button pins on MCU to match output order
    [DigitalLabBoard.PrjPCB, DigitalLabBoard_Processor.SchDoc, DigitalLabBoard_Stepper.SchDoc, DigitalLabBoard_Switches.SchDoc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]
2019-11-15 PCB - Provision for extra feet, DNP resistor across USB data lines
    [DigitalLabBoard_Processor.SchDoc]
2019-11-16 PCB - Re-arranged Tvdd sampling and combined with discharge. Removed USB 0R resistor as not needed.
    [DigitalLabBoard.PrjPCB, DigitalLabBoard_Processor.SchDoc]
2019-11-16 Review of code - Delayed power-on and separated from TVdd monitoring time. Needed due to slow startup of OLED. - Added TVdd discharge. Provides somewhere for regulator leakage current to go when off.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
2019-11-17 Review of code - Fixed power on for MotorSimulator - Minor tweaks
2019-11-18 Minor tweaks
    [BOM - Edited.xls]
2019-11-28 Added nalclip to protect Gnd connection
    [BOM - Edited.xls, Bill of Materials-DigitalLabBoard.xls, DigitalLabBoard.GBL, DigitalLabBoard.GBO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]
2019-12-06 PCB V2 - Add nalclip for ground edge - Increase clearance around uC for hand soldering. - Re-arranged components below LCD so it sits flatter - Changed TVS to PRTR5V0U4D,125 - Changed 1 GPIO expander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
    [BOM - Edited.xls, Bill of Materials-DigitalLabBoard.xls, DigitalLabBoard.GBL, DigitalLabBoard.GBO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]
2019-12-07 PCB V2 - Re-arranged components below LCD so it sits flatter (again) - Re-routed USB tracks so shorter and minimized crossings.
    [DigitalLabBoard.PrjPCB, DigitalLabBoard_LEDs.SchDoc, DigitalLabBoard_Processor.SchDoc]
2019-12-11 PCB V2 - Manufacture
    [BOM - Edited.xls, DigitalLabBoard.PrjPCB, DigitalLabBoard_Processor.SchDoc]
2019-12-17 General Cleanup and re-arrangement
    [BOM - Edited.xls]
2019-12-26 Hardware V3 - Added JTAG interface for CPLD programming
    [BOM - Edited.xls, DigitalLabBoard.PrjPCB, DigitalLabBoard_Die.SchDoc, DigitalLabBoard_LEDs.SchDoc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]
2019-12-31 Hardware V3 - Changed connector gender, widened JTAG area
    [BOM - Edited.xls, DigitalLabBoard.PrjPCB, DigitalLabBoard_Die.SchDoc, DigitalLabBoard_LEDs.SchDoc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]
2020-01-02 Hardware V3 Manufacture
    [BOM - Edited.xls, Bill of Materials-DigitalLabBoard.csv, Copy of DigitalLabBoard_Jig_Milling.PcbDoc, DigitalLabBoard.GBL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]
2020-01-10 Hardware V3 - Added OLED protector
    [BOM - Edited.xls, Bill of Materials-DigitalLabBoard.csv, Copy of DigitalLabBoard_Jig_Milling.PcbDoc, DigitalLabBoard.GBL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]
2020-01-11 Hardware V3 - More tweaks
    [DigitalLabBoard.PrjPCB]
2020-01-25 Hardware V4 - OLED Shield changes
    [BOM - Edited.xls, DigitalLabBoard_Die.SchDoc, DigitalLabBoard_Jig.PcbDoc, DigitalLabBoard_LEDs.SchDoc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]
2020-07-05 Misc Sync
    [BOM - Edited.xls, Bill of Materials-DigitalLabBoard.csv, DigitalLabBoard.GBL, DigitalLabBoard.GBO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]
2020-09-15 Folded CPLD programmer project in
    [BOM - Edited.xls, Bill of Materials-CPLD_Programmer.xls, Bill of Materials-DigitalLabBoard.csv, CPLD_Programmer.GBL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]
2021-01-19 Updated PDF, Exported PCB in V5 format
    [CPLD_Programmer-CS.PcbDoc, DigitalLabBoard-CS.PcbDoc]
2021-05-14 Improved handling of LEDs on hardware on certain error situations.
2021-08-01 PCB - Cosmetic changes schematics and PDF format
    [DigitalLabBoard_Die.SchDoc, DigitalLabBoard_LEDs.SchDoc, DigitalLabBoard_Processor.SchDoc, DigitalLabBoard_Switches.SchDoc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]
2022-01-05 Software - Revamp of bootloader - now supports two flash regions so allows use of all of the flash on Kinetis MKxxDX devices.
2022-02-20 Added Board Image
2023-02-03 Software - Minor GUI changes to CPLD programmer
    [cpld_tester_pad.csv]
2023-02-09 Software - Programmer now remembers path to last used file on Linux
    [cpld_tester_pad.csv]
2023-02-20 Firmware - Changes to protect I2C from soft power-on transients on SCL/SDA.
